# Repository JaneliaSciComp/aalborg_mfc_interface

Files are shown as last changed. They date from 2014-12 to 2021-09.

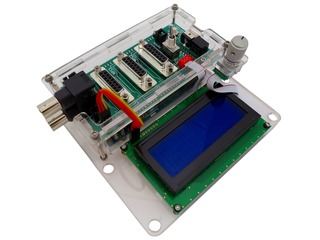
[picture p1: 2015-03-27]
images/aalborg_mfc_interface_03_s.jpg

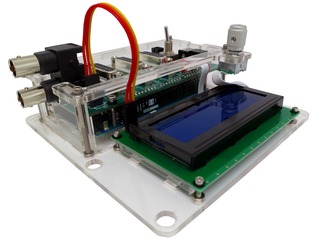
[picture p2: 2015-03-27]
images/aalborg_mfc_interface_04_s.jpg

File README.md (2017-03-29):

# aalborg_mfc_interface

Authors:

    Peter Polidoro <polidorop@janelia.hhmi.org>

License:

    BSD

## More Detailed Help on Installation and Usage

[modular-devices](https://github.com/janelia-modular-devices/modular-devices)

## Device Information

```json
{
  "method":"?",
  "device_info":{
    "name":"aalborg_mfc_interface",
    "model_number":1100,
    "serial_number":0,
    "firmware_version":{
      "major":0,
      "minor":1,
      "patch":0
    }
  },
  "methods":[
    "getMemoryFree",
    "resetDefaults",
    "setSerialNumber",
    "executeStandaloneCallback",
    "getLedsPowered",
    "setMfcFlow",
    "setMfcFlows",
    "getMfcFlowSetting",
    "getMfcFlowSettings",
    "getMfcFlowMeasure",
    "getMfcFlowMeasures",
    "getAnalogInput",
    "getAnalogInputs",
    "saveState",
    "recallState",
    "getSavedStates",
    "pulseBncB"
  ],
  "status":success
}
```

## Verbose Device Information

```json
{
  "method":"??",
  "device_info":{
    "name":"aalborg_mfc_interface",
    "model_number":1100,
    "serial_number":0,
    "firmware_version":{
      "major":0,
      "minor":1,
      "patch":0
    }
  },
  "methods":[
    {
      "name":"getMemoryFree",
      "parameters":[]
    },
    {
      "name":"resetDefaults",
      "parameters":[]
    },
    {
      "name":"setSerialNumber",
      "parameters":[
        {
          "name":"serial_number",
          "type":"long",
          "min":0,
          "max":65535
        }
      ]
    },
    {
      "name":"executeStandaloneCallback",
      "parameters":[]
    },
    {
      "name":"getLedsPowered",
      "parameters":[]
    },
    {
      "name":"setMfcFlow",
      "parameters":[
        {
          "name":"mfc",
          "type":"long",
          "min":0,
          "max":2
        },
        {
          "name":"percent",
          "type":"long",
          "min":0,
          "max":100
        }
      ]
    },
    {
      "name":"setMfcFlows",
      "parameters":[
        {
          "name":"percents",
          "type":"array",
          "array_element_type":"long",
          "min":0,
          "max":100
        }
      ]
    },
    {
      "name":"getMfcFlowSetting",
      "parameters":[
        {
          "name":"mfc",
          "type":"long",
          "min":0,
          "max":2
        }
      ]
    },
    {
      "name":"getMfcFlowSettings",
      "parameters":[]
    },
    {
      "name":"getMfcFlowMeasure",
      "parameters":[
        {
          "name":"mfc",
          "type":"long",
          "min":0,
          "max":2
        }
      ]
    },
    {
      "name":"getMfcFlowMeasures",
      "parameters":[]
    },
    {
      "name":"getAnalogInput",
      "parameters":[
        {
          "name":"ain",
          "type":"long",
          "min":0,
          "max":2
        }
      ]
    },
    {
      "name":"getAnalogInputs",
      "parameters":[]
    },
    {
      "name":"saveState",
      "parameters":[
        {
          "name":"state",
          "type":"long",
          "min":0,
          "max":9
        }
      ]
    },
    {
      "name":"recallState",
      "parameters":[
        {
          "name":"state",
          "type":"long",
          "min":0,
          "max":9
        }
      ]
    },
    {
      "name":"getSavedStates",
      "parameters":[]
    },
    {
      "name":"pulseBncB",
      "parameters":[
        {
          "name":"duration",
          "units":"ms",
          "type":"long",
          "min":1,
          "max":10000
        }
      ]
    }
  ],
  "status":success
}
```

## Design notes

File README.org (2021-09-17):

#+TITLE: aalborg_mfc_interface
#+AUTHOR: Peter Polidoro
#+EMAIL: peter@polidoro.io

* Repository Information
  - Author :: Peter Polidoro
  - License :: BSD

* More Detailed Help on Installation and Usage

   [[https://github.com/janelia-modular-devices/modular-devices][modular-devices]]

* Device Information

   #+BEGIN_SRC js
{
  "method":"?",
  "device_info":{
    "name":"aalborg_mfc_interface",
    "model_number":1100,
    "serial_number":0,
    "firmware_version":{
      "major":0,
      "minor":1,
      "patch":0
    }
  },
  "methods":[
    "getMemoryFree",
    "resetDefaults",
    "setSerialNumber",
    "executeStandaloneCallback",
    "getLedsPowered",
    "setMfcFlow",
    "setMfcFlows",
    "getMfcFlowSetting",
    "getMfcFlowSettings",
    "getMfcFlowMeasure",
    "getMfcFlowMeasures",
    "getAnalogInput",
    "getAnalogInputs",
    "saveState",
    "recallState",
    "getSavedStates",
    "pulseBncB"
  ],
  "status":success
}
   #+END_SRC

* Verbose Device Information

   #+BEGIN_SRC js
{
  "method":"??",
  "device_info":{
    "name":"aalborg_mfc_interface",
    "model_number":1100,
    "serial_number":0,
    "firmware_version":{
      "major":0,
      "minor":1,
      "patch":0
    }
  },
  "methods":[
    {
      "name":"getMemoryFree",
      "parameters":[]
    },
    {
      "name":"resetDefaults",
      "parameters":[]
    },
    {
      "name":"setSerialNumber",
      "parameters":[
        {
          "name":"serial_number",
          "type":"long",
          "min":0,
          "max":65535
        }
      ]
    },
    {
      "name":"executeStandaloneCallback",
      "parameters":[]
    },
    {
      "name":"getLedsPowered",
      "parameters":[]
    },
    {
      "name":"setMfcFlow",
      "parameters":[
        {
          "name":"mfc",
          "type":"long",
          "min":0,
          "max":2
        },
        {
          "name":"percent",
          "type":"long",
          "min":0,
          "max":100
        }
      ]
    },
    {
      "name":"setMfcFlows",
      "parameters":[
        {
          "name":"percents",
          "type":"array",
          "array_element_type":"long",
          "min":0,
          "max":100
        }
      ]
    },
    {
      "name":"getMfcFlowSetting",
      "parameters":[
        {
          "name":"mfc",
          "type":"long",
          "min":0,
          "max":2
        }
      ]
    },
    {
      "name":"getMfcFlowSettings",
      "parameters":[]
    },
    {
      "name":"getMfcFlowMeasure",
      "parameters":[
        {
          "name":"mfc",
          "type":"long",
          "min":0,
          "max":2
        }
      ]
    },
    {
      "name":"getMfcFlowMeasures",
      "parameters":[]
    },
    {
      "name":"getAnalogInput",
      "parameters":[
        {
          "name":"ain",
          "type":"long",
          "min":0,
          "max":2
        }
      ]
    },
    {
      "name":"getAnalogInputs",
      "parameters":[]
    },
    {
      "name":"saveState",
      "parameters":[
        {
          "name":"state",
          "type":"long",
          "min":0,
          "max":9
        }
      ]
    },
    {
      "name":"recallState",
      "parameters":[
        {
          "name":"state",
          "type":"long",
          "min":0,
          "max":9
        }
      ]
    },
    {
      "name":"getSavedStates",
      "parameters":[]
    },
    {
      "name":"pulseBncB",
      "parameters":[
        {
          "name":"duration",
          "units":"ms",
          "type":"long",
          "min":1,
          "max":10000
        }
      ]
    }
  ],
  "status":success
}
   #+END_SRC

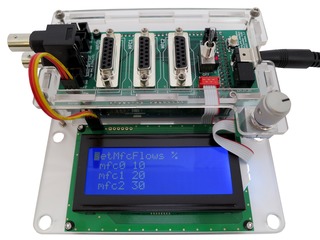
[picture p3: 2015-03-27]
images/aalborg_mfc_interface_06_s.jpg

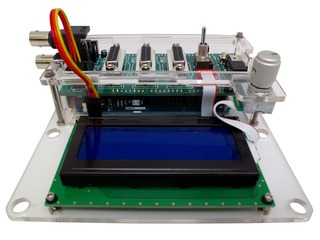
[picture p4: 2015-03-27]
images/aalborg_mfc_interface_05_s.jpg

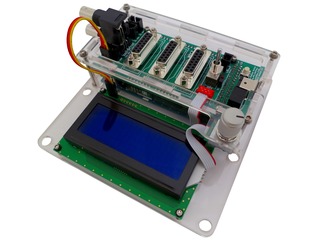
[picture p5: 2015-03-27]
images/aalborg_mfc_interface_01_s.jpg

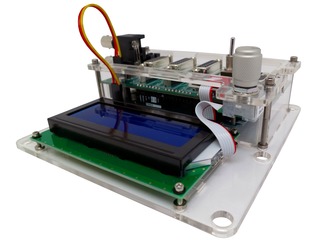
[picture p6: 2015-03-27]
images/aalborg_mfc_interface_02_s.jpg

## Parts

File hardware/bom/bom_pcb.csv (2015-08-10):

Item | Reference(s) | Value | Quantity | Description | PartNumber | Vendor
1 | ARDUINO1 | ARDUINO_MEGA | 1 | BOARD MCU MEGA2560 | 1050-1018-ND | digikey
2 | C1 C2 C3 C6 C7 C8 | 10uF | 6 | CAP CER 10UF 50V 10% X7S 1210 | 445-4536-1-ND | digikey
3 | C4 C5 | 0.1uF | 2 | CAP CER 0.1UF 50V 10% X7R 1210 | 478-3586-1-ND | digikey
4 | D1 | LED_24V | 1 | LED 2MM 24V VERTICAL RED PC MNT | 350-1723-ND | digikey
5 | E1 | ENCODER_C14 | 1 | CONN FMALE-ON-BRD 6POS VERT SMD | A99474CT-ND | digikey
6 | J1 J2 J3 | DB15FV | 3 | CONN D-SUB RCPT 15POS VERT GOLD | A102054-ND | digikey
7 | P1 | PWR_JACK_2.5x5.5 | 1 | CONN PWR JACK DC 2.5X5.5 8A T/H | CP-063BH-ND | digikey
8 | P2 | HEADER_01X03 | 1 | 01x03 .100 SR STRAIGHT | 609-3461-ND | digikey
9 | P3 | BNC_DOUBLE_RA | 1 | CONN BNC JACK R/A 75 OHM PCB | ACX1655-ND | digikey
10 | P4 P5 P6 | HEADER_01X03_SHR | 3 | CONN HEADER 3POS .100 VERT GOLD | WM4801-ND | digikey
11 | R1 R2 R3 R4 R5 | 5.11k | 5 | RES SMD 5.11K OHM 1% 1/2W 1210 | P5.11KAACT-ND | digikey
12 | REG1 | CONV_DC_DC_12V_1A | 1 | CONV DC/DC 1A 12V OUT SIP VERT | 945-1392-5-ND | digikey
13 | S1 | HEADER_01X02_SHR | 1 | CONN HEADER 2POS .100 VERT GOLD | WM4800-ND | digikey
14 | SW1 | DPST_SERIES_M | 1 | SWITCH TOGGLE DPST 6A 125V | 360-3244-ND | digikey
15 | SW2 | KT_SWITCH | 1 | SWITCH TACTILE SPST-NO 1VA 32V | CKN1860CT-ND | digikey
16 | U1 U2 | MAX6817 | 2 | IC DEBOUNCER SWITCH DUAL SOT23-6 | MAX6817EUT+TCT-ND | digikey

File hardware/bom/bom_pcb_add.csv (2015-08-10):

Item | Function | Quantity | Description | PartNumber | Vendor
1 | ARDUINO | 2 | CONN HDR VERT 50POS .100 SNGL | SAM1055-50-ND | digikey
2 | ARDUINO | 1 | CABLE USB A-B MALE 1M 2.0 VERS | AE1462-ND | digikey
3 | POWER | 1 | AC/DC DESKTOP ADAPTER 24V 100W | 271-2728-ND | digikey
4 | POWER | 1 | LINE CORD 3 COND US | 993-1039-ND | digikey
5 | DISPLAY | 1 | LCD SERIAL 4X20 SIDE WHT BKLT | NHD-0420D3Z-NSW-BBW-V3-ND | digikey
6 | DISPLAY | 1 | 01x03 .100 SR STRAIGHT | 609-3461-ND | digikey
7 | DISPLAY | 1 | Jumper Wire - 0.1in 3-pin 4in | PRT-10363 | sparkfun
8 | ENCODER_C14 | 1 | ENCODER OPT 32PPR DET CABLE TYPE | 102-1914-ND | digikey
9 | ENCODER_C14 | 1 | KNOB CLR/MATTE.50 DIA .250 SHAFT | 226-3100-ND | digikey
10 | MFC | 2 | ASSEMBLED D-SUB CABLE 15-POS | 277-7325-ND | digikey

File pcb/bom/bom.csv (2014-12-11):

Source: aalborg_mfc_interface.sch
Date: Wed 10 Dec 2014 05:16:41 PM EST
Item | Reference(s) | Value | Quantity | Description | PartNumber | Vendor
1 | ARDUINO1 | ARDUINO_MEGA | 1 | 1050-1018-ND | digikey
2 | C1 C2 C3 C5 C6 | 10uF | 5 | 445-4536-1-ND | digikey
3 | C4 | 0.1uF | 1 | 478-3586-1-ND | digikey
4 | D1 | LED_24V | 1 | 350-1723-ND | digikey
5 | E1 | ENCODER_C14 | 1 | 102-1914-ND | digikey
6 | J1 J2 | DB15FV | 2 | A102054-ND | digikey
7 | P1 | PWR_JACK_2.5x5.5 | 1 | CP-063BH-ND | digikey
8 | P2 | HEADER_01X03 | 1 | 609-3461-ND | digikey
9 | R1 R2 R3 R4 | 5.11k | 4 | P5.11KAACT-ND | digikey
10 | REG1 | CONV_DC_DC_12V_1A | 1 | 945-1392-5-ND | digikey
11 | U1 | MAX6817 | 1 | MAX6817EUT+TCT-ND | digikey

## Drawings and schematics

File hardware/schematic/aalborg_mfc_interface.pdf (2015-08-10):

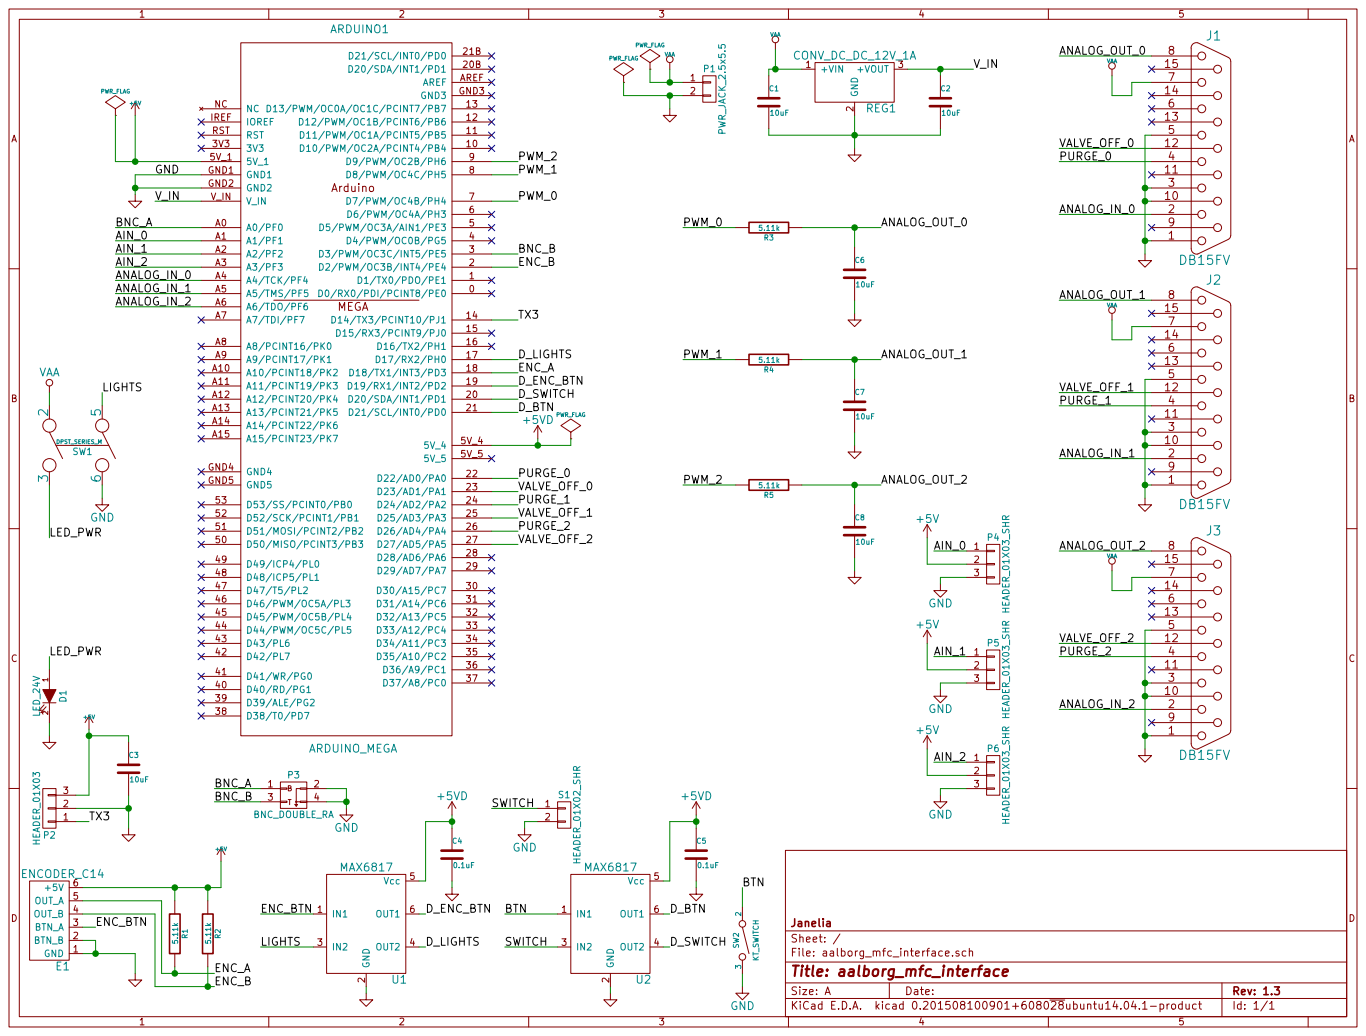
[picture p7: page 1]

File: aalborg_mfc_interface.sch Sheet: / Janelia

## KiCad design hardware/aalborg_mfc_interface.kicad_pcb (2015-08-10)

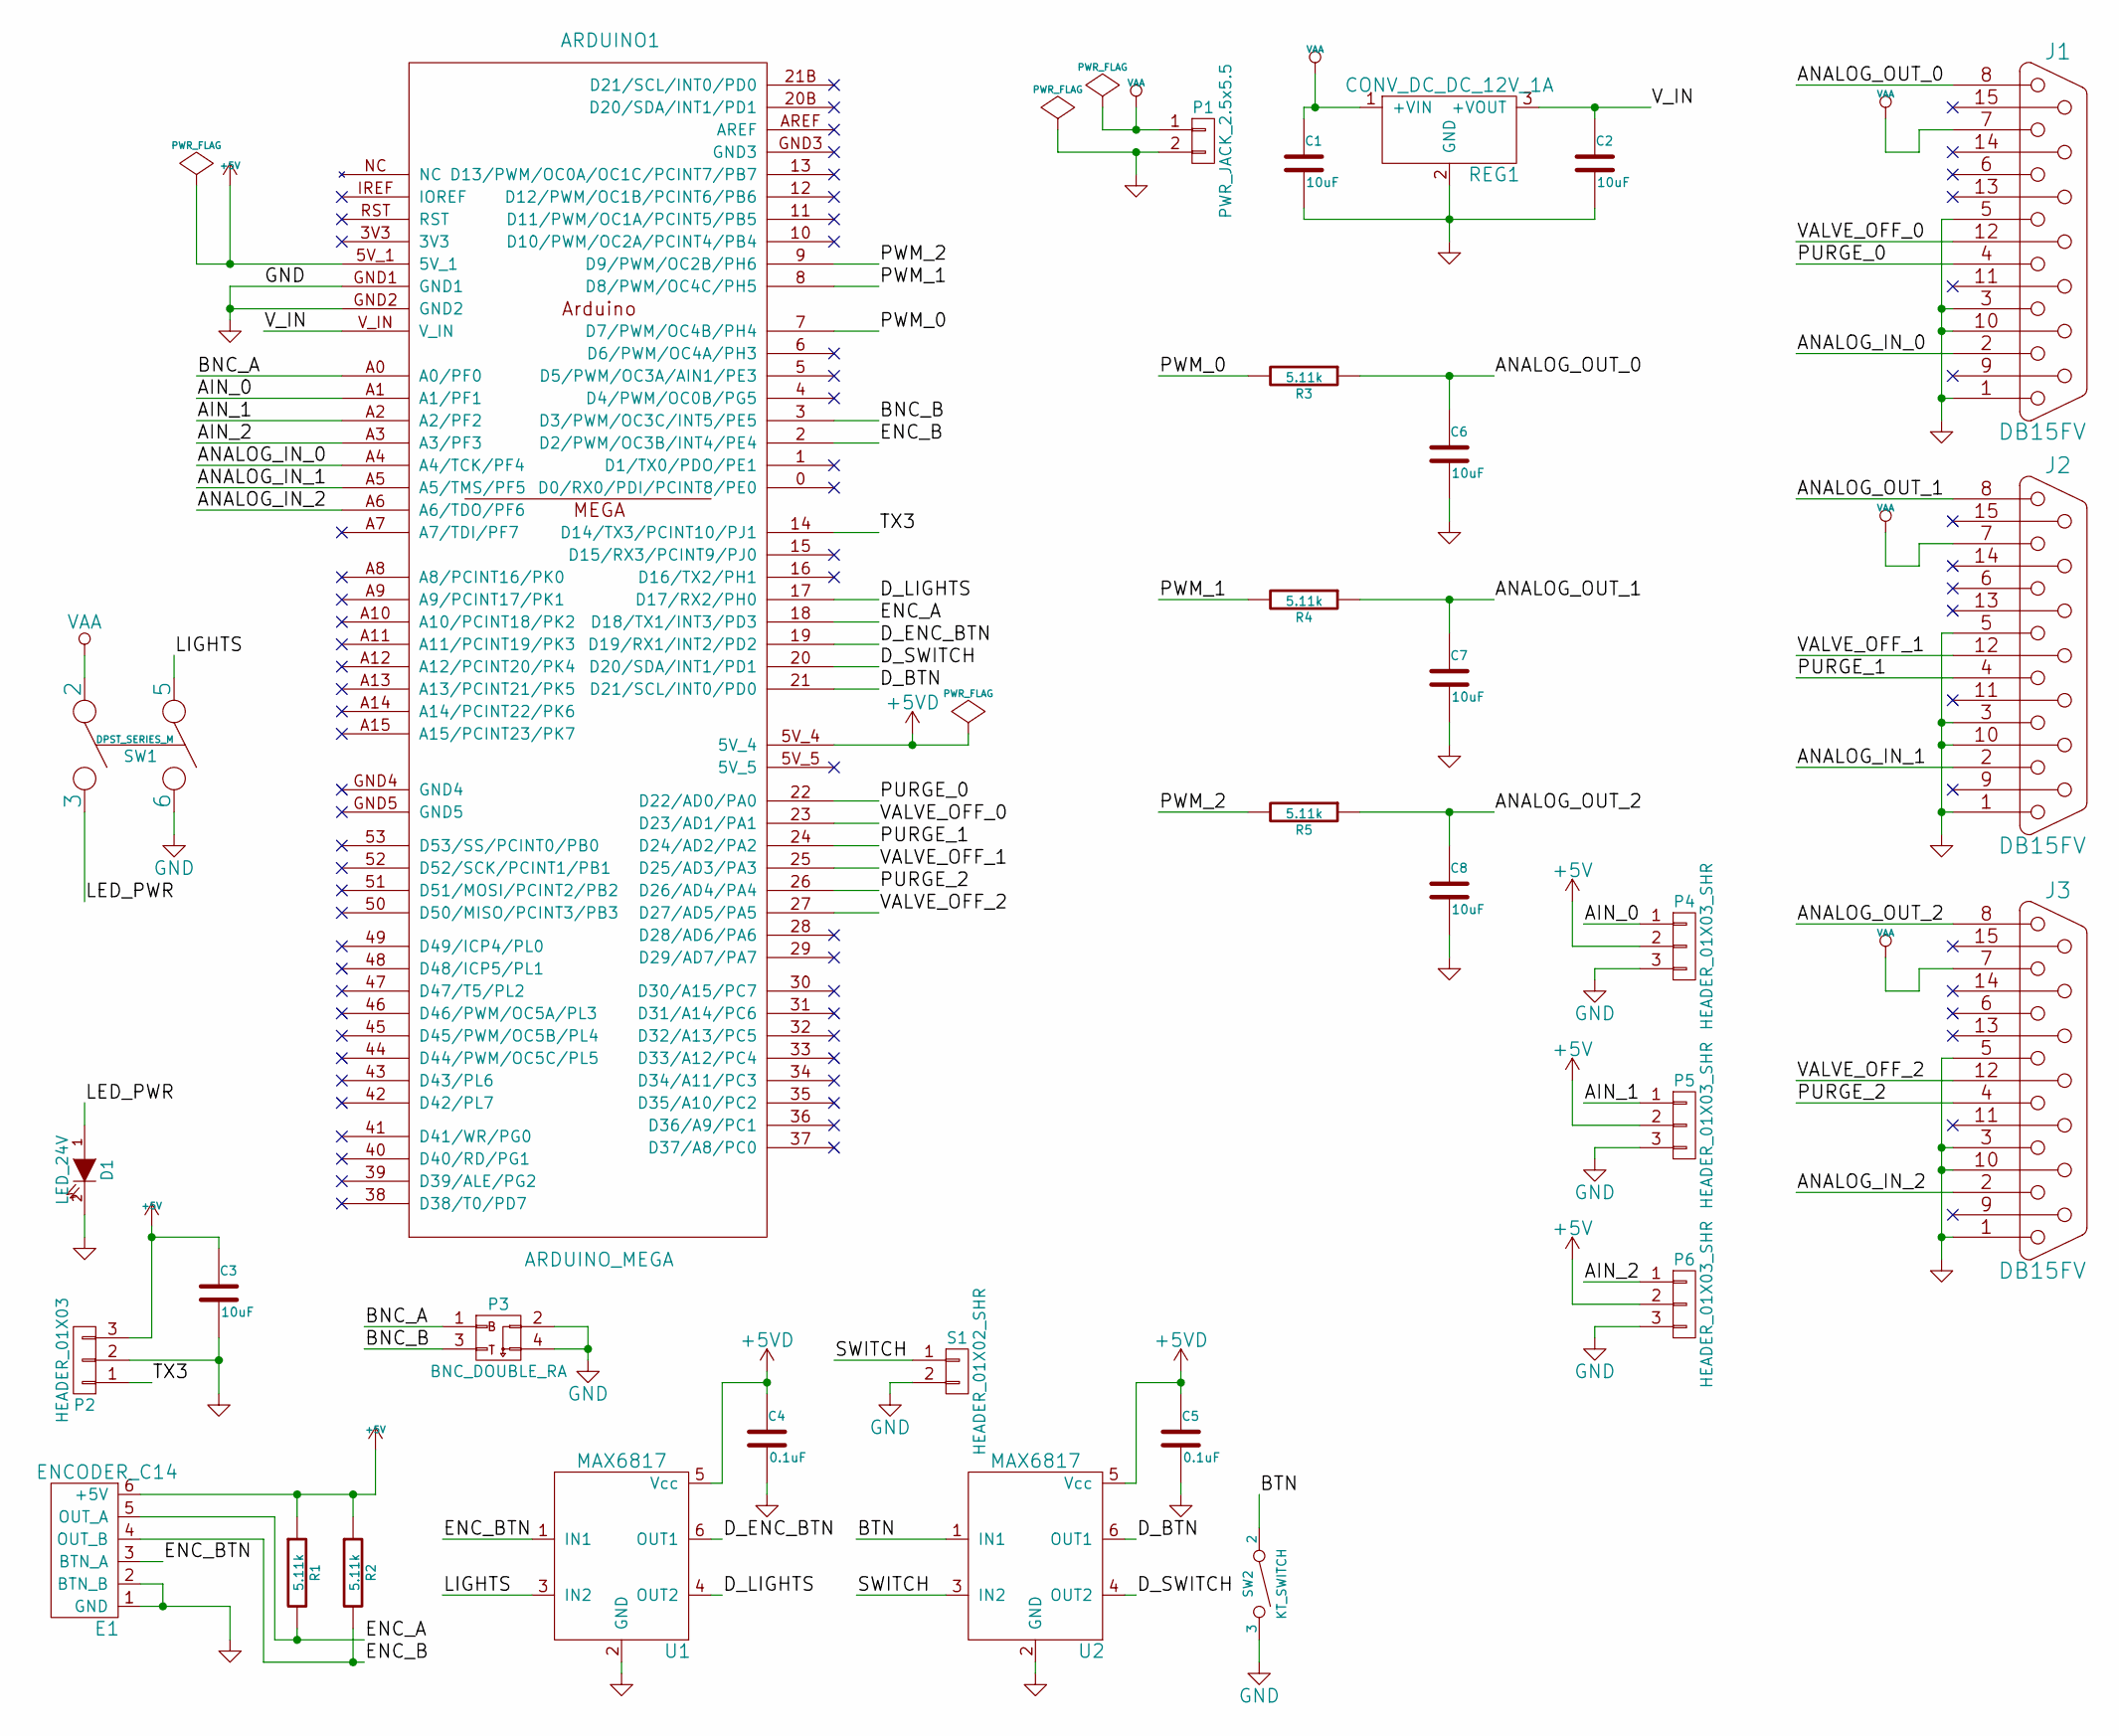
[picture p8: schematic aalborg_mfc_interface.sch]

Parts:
ARDUINO1: ARDUINO_MEGA; ARDUINO_MEGA_SHIELD; PartNumber 1050-1018-ND
C1, C2, C3, C6, C7, C8: 10uF; SM1210; PartNumber 445-4536-1-ND
C4, C5: 0.1uF; SM1210; PartNumber 478-3586-1-ND
D1: LED_24V; LED_555-3XXX; PartNumber 350-1723-ND
E1: ENCODER_C14; Micro-MaTch_6_SMD; PartNumber A99474CT-ND
J1, J2, J3: DB15FV; DB15FD; PartNumber A102054-ND
P1: PWR_JACK_2.5x5.5; DCJACK_2PIN_HIGHCURRENT; PartNumber CP-063BH-ND
P2: HEADER_01X03; Header_3_Pin; PartNumber 609-3461-ND
P3: BNC_DOUBLE_RA; BNC_DOUBLE; PartNumber ACX1655-ND
P4, P5, P6: HEADER_01X03_SHR; Header_Shrouded_3_Pin; PartNumber WM4801-ND
R1, R2, R3, R4, R5: 5.11k; SM1210; PartNumber P5.11KAACT-ND
REG1: CONV_DC_DC_12V_1A; DC_DC_CONV_R78C; PartNumber 945-1392-5-ND
S1: HEADER_01X02_SHR; Header_Shrouded_2_Pin; PartNumber WM4800-ND
SW1: DPST_SERIES_M; PartNumber 360-3244-ND
SW2: KT_SWITCH; PartNumber CKN1860CT-ND
U1, U2: MAX6817; PartNumber MAX6817EUT+TCT-ND

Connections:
+5V: ARDUINO1.5V_1, C3.1, E1.6 (+5V), P2.3, P4.2, P5.2, P6.2, R1.1, R2.1
+5VD: ARDUINO1.5V_4, C4.1, C5.1, U1.5 (Vcc), U2.5 (Vcc)
/AIN_0: ARDUINO1.A1 (A1/PF1), P4.1
/AIN_1: ARDUINO1.A2 (A2/PF2), P5.1
/AIN_2: ARDUINO1.A3 (A3/PF3), P6.1
/ANALOG_IN_0: ARDUINO1.A4 (A4/TCK/PF4), J1.2
/ANALOG_IN_1: ARDUINO1.A5 (A5/TMS/PF5), J2.2
/ANALOG_IN_2: ARDUINO1.A6 (A6/TDO/PF6), J3.2
/ANALOG_OUT_0: C6.1, J1.8, R3.1
/ANALOG_OUT_1: C7.1, J2.8, R4.1
/ANALOG_OUT_2: C8.1, J3.8, R5.1
/BNC_A: ARDUINO1.A0 (A0/PF0), P3.1
/BNC_B: ARDUINO1.3 (D3/PWM/OC3C/INT5/PE5), P3.3
/BTN: SW2.2, U2.1 (IN1)
/D_BTN: ARDUINO1.21 (D21/SCL/INT0/PD0), U2.6 (OUT1)
/D_ENC_BTN: ARDUINO1.19 (D19/RX1/INT2/PD2), U1.6 (OUT1)
/D_LIGHTS: ARDUINO1.17 (D17/RX2/PH0), U1.4 (OUT2)
/D_SWITCH: ARDUINO1.20 (D20/SDA/INT1/PD1), U2.4 (OUT2)
/ENC_A: ARDUINO1.18 (D18/TX1/INT3/PD3), E1.5 (OUT_A), R1.2
/ENC_B: ARDUINO1.2 (D2/PWM/OC3B/INT4/PE4), E1.4 (OUT_B), R2.2
/ENC_BTN: E1.3 (BTN_A), U1.1 (IN1)
/LED_PWR: D1.1 (A), SW1.3
/LIGHTS: SW1.5, U1.3 (IN2)
/PURGE_0: ARDUINO1.22 (D22/AD0/PA0), J1.4
/PURGE_1: ARDUINO1.24 (D24/AD2/PA2), J2.4
/PURGE_2: ARDUINO1.26 (D26/AD4/PA4), J3.4
/PWM_0: ARDUINO1.7 (D7/PWM/OC4B/PH4), R3.2
/PWM_1: ARDUINO1.8 (D8/PWM/OC4C/PH5), R4.2
/PWM_2: ARDUINO1.9 (D9/PWM/OC2B/PH6), R5.2
/SWITCH: S1.1, U2.3 (IN2)
/TX3: ARDUINO1.14 (D14/TX3/PCINT10/PJ1), P2.1
/VALVE_OFF_0: ARDUINO1.23 (D23/AD1/PA1), J1.12
/VALVE_OFF_1: ARDUINO1.25 (D25/AD3/PA3), J2.12
/VALVE_OFF_2: ARDUINO1.27 (D27/AD5/PA5), J3.12
/V_IN: ARDUINO1.V_IN, C2.1, REG1.3 (+VOUT)
GND: ARDUINO1.GND1, ARDUINO1.GND2, C1.2, C2.2, C3.2, C4.2, C5.2, C6.2, C7.2, C8.2, D1.2 (K), E1.1 (GND), E1.2 (BTN_B), J1.1, J1.3, J1.5, J1.10, J2.1, J2.3, J2.5, J2.10, J3.1, J3.3, J3.5, J3.10, P1.2, P2.2, P3.2, P3.4, P4.3, P5.3, P6.3, REG1.2 (GND), S1.2, SW1.6, SW2.3, U1.2 (GND), U2.2 (GND)
VAA: C1.1, J1.7, J2.7, J3.7, P1.1, REG1.1 (+VIN), SW1.2

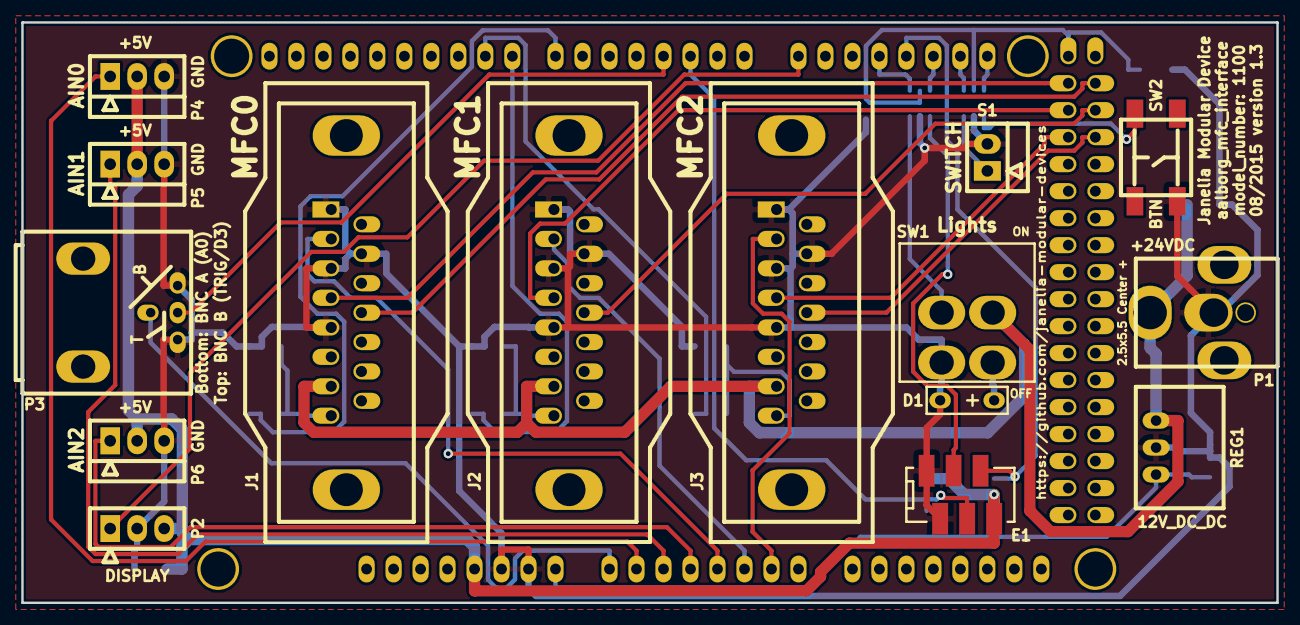
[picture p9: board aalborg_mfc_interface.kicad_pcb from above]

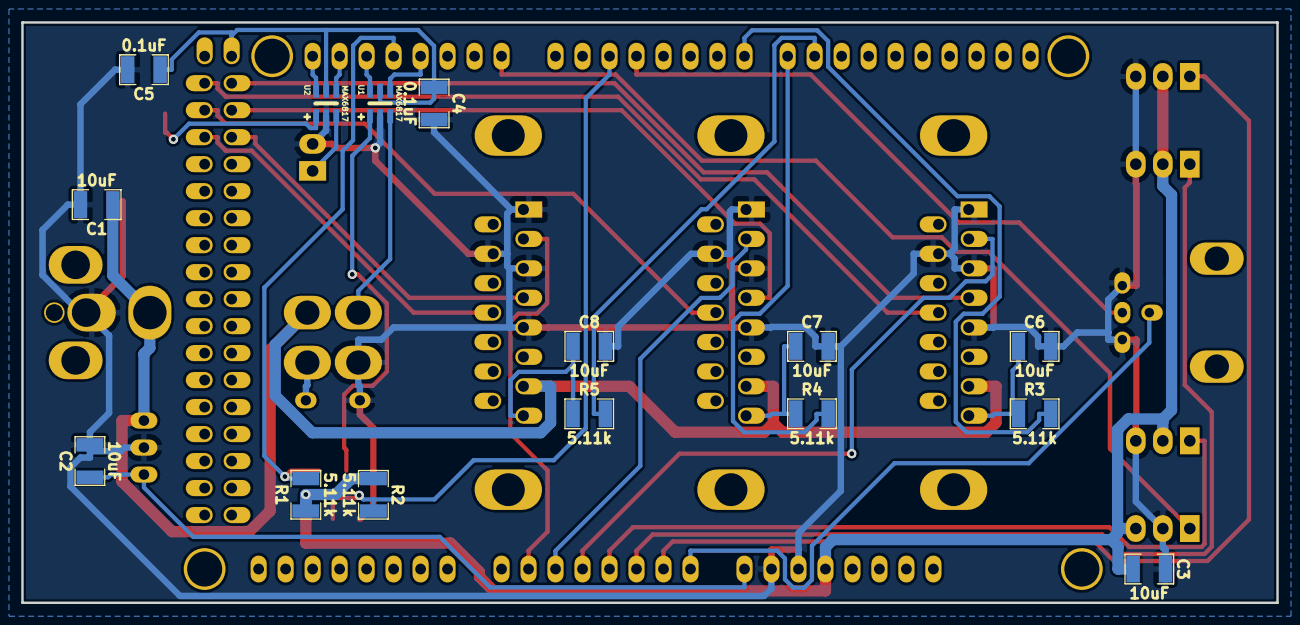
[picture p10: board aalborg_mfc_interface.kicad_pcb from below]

Board: 2 copper layers, 118.1 x 54.6 mm, 31 parts (15 on the bottom side), 37 nets.

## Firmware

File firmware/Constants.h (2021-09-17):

// ----------------------------------------------------------------------------
// Constants.h
//
//
// Authors:
// Peter Polidoro peter@polidoro.io
// ----------------------------------------------------------------------------
#ifndef CONSTANTS_H
#define CONSTANTS_H
#include "ConstantVariable.h"

namespace constants
{
enum {FRAME_COUNT=6};
enum {STATE_COUNT=10};
enum {MFC_COUNT=3};
enum {AIN_COUNT=3};

extern const unsigned int baudrate;

extern const unsigned int model_number;

extern const unsigned char firmware_major;
extern const unsigned char firmware_minor;
extern const unsigned char firmware_patch;

extern HardwareSerial & display_serial;

extern const int enc_a_pin;
extern const int enc_b_pin;
extern const int enc_btn_pin;
extern const int enc_btn_int;
extern const int btn_pin;
extern const int btn_int;
extern const int lights_pin;
extern const int bnc_b_pin;
extern const int standalone_update_period;

extern const int mfc_pwm_pins[MFC_COUNT];
extern const int mfc_ain_pins[MFC_COUNT];
extern const int mfc_purge_pins[MFC_COUNT];
extern const int mfc_valve_off_pins[MFC_COUNT];

extern const int ain_pins[AIN_COUNT];

extern const int pwm_min;
extern const int pwm_max;
extern const int ain_min;
extern const int ain_max;

extern const int percent_min;
extern const int percent_max;

extern const uint8_t states_array_default[STATE_COUNT][MFC_COUNT];

extern const uint8_t mfc_dsp_lbl_display_positions[MFC_COUNT];
extern const uint8_t ain_dsp_lbl_display_positions[AIN_COUNT];
extern const uint8_t state_dsp_lbl_display_position;
extern const uint8_t duration_dsp_lbl_display_position;

extern const uint8_t percent_display_width;

extern const uint8_t flow_var_display_positions[MFC_COUNT];
extern const uint8_t ain_dsp_var_display_positions[AIN_COUNT];
extern const uint8_t state_int_var_display_position;
extern const uint8_t duration_int_var_display_position;
extern const uint16_t duration_int_var_default;

extern const uint16_t duration_min;
extern const uint16_t duration_max;

extern ConstantString device_name;

extern ConstantString mfc_parameter_name;
extern ConstantString ain_parameter_name;
extern ConstantString percent_parameter_name;
extern ConstantString percents_parameter_name;
extern ConstantString state_parameter_name;
extern ConstantString duration_parameter_name;
extern ConstantString duration_parameter_units;

extern ConstantString execute_standalone_callback_method_name;
extern ConstantString get_leds_powered_method_name;
extern ConstantString set_mfc_flow_method_name;
extern ConstantString set_mfc_flows_method_name;
extern ConstantString get_mfc_flow_setting_method_name;
extern ConstantString get_mfc_flow_settings_method_name;
extern ConstantString get_mfc_flow_measure_method_name;
extern ConstantString get_mfc_flow_measures_method_name;
extern ConstantString get_analog_input_method_name;
extern ConstantString get_analog_inputs_method_name;
extern ConstantString save_state_method_name;
extern ConstantString recall_state_method_name;
extern ConstantString get_saved_states_method_name;
extern ConstantString pulse_bnc_b_method_name;

extern ConstantString states_name;
extern ConstantString frame0_name;
extern ConstantString frame1_name;
extern ConstantString frame2_name;
extern const ConstantString frame_name_array[FRAME_COUNT];
extern ConstantString mfc0_dsp_lbl_string;
extern ConstantString mfc1_dsp_lbl_string;
extern ConstantString mfc2_dsp_lbl_string;
extern const ConstantString mfc_dsp_lbl_strings[MFC_COUNT];
extern ConstantString ain0_dsp_lbl_string;
extern ConstantString ain1_dsp_lbl_string;
extern ConstantString ain2_dsp_lbl_string;
extern const ConstantString ain_dsp_lbl_strings[AIN_COUNT];
}
#endif

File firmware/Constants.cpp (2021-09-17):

// ----------------------------------------------------------------------------
// Constants.cpp
//
//
// Authors:
// Peter Polidoro peter@polidoro.io
// ----------------------------------------------------------------------------
#include "Constants.h"


namespace constants
{
const unsigned int baudrate = 9600;

const unsigned int model_number = 1100;

// Use semantic versioning http://semver.org/
const unsigned char firmware_major = 0;
const unsigned char firmware_minor = 1;
const unsigned char firmware_patch = 0;

HardwareSerial & display_serial = Serial3;

const int enc_a_pin = 18;
const int enc_b_pin = 2;
const int enc_btn_pin = 19;
const int enc_btn_int = 4;
const int btn_pin = 21;
const int btn_int = 2;
const int lights_pin = 17;
const int bnc_b_pin = 3;
const int standalone_update_period = 300;

const int mfc_pwm_pins[] = {7,8,9};
const int mfc_ain_pins[] = {4,5,6};
const int mfc_purge_pins[] = {22,24,26};
const int mfc_valve_off_pins[] = {23,25,27};

const int ain_pins[] = {1,2,3};

const int pwm_min = 0;
const int pwm_max = 255;
const int ain_min = 0;
const int ain_max = 1023;

const int percent_min = 0;
const int percent_max = 100;

const uint8_t states_array_default[STATE_COUNT][MFC_COUNT] = {0};

const uint8_t mfc_dsp_lbl_display_positions[] = {24,44,64};
const uint8_t ain_dsp_lbl_display_positions[] = {24,44,64};
const uint8_t state_dsp_lbl_display_position = 51;
const uint8_t duration_dsp_lbl_display_position = 49;

const uint8_t percent_display_width = 3;

const uint8_t flow_var_display_positions[] = {26,46,66};
const uint8_t ain_dsp_var_display_positions[] = {26,46,66};
const uint8_t state_int_var_display_position = 57;
const uint8_t duration_int_var_display_position = 51;
const uint16_t duration_int_var_default = 10;

const uint16_t duration_min = 1;
const uint16_t duration_max = 10000;

CONSTANT_STRING(device_name,"aalborg_mfc_interface");

CONSTANT_STRING(mfc_parameter_name,"mfc");
CONSTANT_STRING(ain_parameter_name,"ain");
CONSTANT_STRING(percent_parameter_name,"percent");
CONSTANT_STRING(percents_parameter_name,"percents");
CONSTANT_STRING(state_parameter_name,"state");
CONSTANT_STRING(duration_parameter_name,"duration");
CONSTANT_STRING(duration_parameter_units,"ms");

CONSTANT_STRING(execute_standalone_callback_method_name,"executeStandaloneCallback");
CONSTANT_STRING(get_leds_powered_method_name,"getLedsPowered");
CONSTANT_STRING(set_mfc_flow_method_name,"setMfcFlow");
CONSTANT_STRING(set_mfc_flows_method_name,"setMfcFlows");
CONSTANT_STRING(get_mfc_flow_setting_method_name,"getMfcFlowSetting");
CONSTANT_STRING(get_mfc_flow_settings_method_name,"getMfcFlowSettings");
CONSTANT_STRING(get_mfc_flow_measure_method_name,"getMfcFlowMeasure");
CONSTANT_STRING(get_mfc_flow_measures_method_name,"getMfcFlowMeasures");
CONSTANT_STRING(get_analog_input_method_name,"getAnalogInput");
CONSTANT_STRING(get_analog_inputs_method_name,"getAnalogInputs");
CONSTANT_STRING(save_state_method_name,"saveState");
CONSTANT_STRING(recall_state_method_name,"recallState");
CONSTANT_STRING(get_saved_states_method_name,"getSavedStates");
CONSTANT_STRING(pulse_bnc_b_method_name,"pulseBncB");

CONSTANT_STRING(states_name,"states");
CONSTANT_STRING(frame0_name,"setMfcFlows %");
CONSTANT_STRING(frame1_name,"getMfcFlowMeasures %");
CONSTANT_STRING(frame2_name,"getAnalogInputs %");
const ConstantString frame_name_array[] =
  {
    frame0_name,
    frame1_name,
    frame2_name,
    save_state_method_name,
    recall_state_method_name,
    pulse_bnc_b_method_name,
  };
CONSTANT_STRING(mfc0_dsp_lbl_string,"mfc0");
CONSTANT_STRING(mfc1_dsp_lbl_string,"mfc1");
CONSTANT_STRING(mfc2_dsp_lbl_string,"mfc2");
const ConstantString mfc_dsp_lbl_strings[] =
  {
    mfc0_dsp_lbl_string,
    mfc1_dsp_lbl_string,
    mfc2_dsp_lbl_string,
  };
CONSTANT_STRING(ain0_dsp_lbl_string,"ain0");
CONSTANT_STRING(ain1_dsp_lbl_string,"ain1");
CONSTANT_STRING(ain2_dsp_lbl_string,"ain2");
const ConstantString ain_dsp_lbl_strings[] =
  {
    ain0_dsp_lbl_string,
    ain1_dsp_lbl_string,
    ain2_dsp_lbl_string,
  };
}

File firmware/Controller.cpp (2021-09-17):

// ----------------------------------------------------------------------------
// Controller.cpp
//
// Authors:
// Peter Polidoro peter@polidoro.io
// ----------------------------------------------------------------------------
#include "Controller.h"

Controller::Controller() :
  standalone_interface_(Standalone::StandaloneInterface(constants::display_serial,
                                                        constants::enc_a_pin,
                                                        constants::enc_b_pin,
                                                        constants::enc_btn_pin,
                                                        constants::enc_btn_int,
                                                        constants::btn_pin,
                                                        constants::btn_int,
                                                        constants::lights_pin,
                                                        constants::standalone_update_period))
{
}

void Controller::setup()
{
  EventController::event_controller.setup();

  // Pin Setup
  for (int mfc = 0; mfc < constants::MFC_COUNT; mfc++)
  {
    pinMode(constants::mfc_purge_pins[mfc],INPUT);
    pinMode(constants::mfc_valve_off_pins[mfc],INPUT);
  }
  pinMode(constants::bnc_b_pin,OUTPUT);

  // Device Info
  modular_device.setName(constants::device_name);
  modular_device.setModelNumber(constants::model_number);
  modular_device.setFirmwareVersion(constants::firmware_major,constants::firmware_minor,constants::firmware_patch);

  // Saved Variables
  modular_device.createSavedVariable(constants::states_name,
                                     constants::states_array_default,
                                     constants::STATE_COUNT);

  int default_state = 0;
  modular_device.getSavedVariableValue(constants::states_name,flow_settings_array_,default_state);
  for (int mfc=0; mfc<constants::MFC_COUNT; mfc++)
  {
    setMfcFlow(mfc,flow_settings_array_[mfc]);
  }

  // Parameters
  ModularDevice::Parameter & mfc_parameter = modular_device.createParameter(constants::mfc_parameter_name);
  mfc_parameter.setRange(0,constants::MFC_COUNT-1);

  ModularDevice::Parameter & ain_parameter = modular_device.createParameter(constants::ain_parameter_name);
  ain_parameter.setRange(0,constants::AIN_COUNT-1);

  ModularDevice::Parameter & percent_parameter = modular_device.createParameter(constants::percent_parameter_name);
  percent_parameter.setRange(constants::percent_min,constants::percent_max);

  ModularDevice::Parameter & percents_parameter = modular_device.createParameter(constants::percents_parameter_name);
  percents_parameter.setTypeArray();
  percents_parameter.setRange(constants::percent_min,constants::percent_max);

  ModularDevice::Parameter & state_parameter = modular_device.createParameter(constants::state_parameter_name);
  state_parameter.setRange(0,constants::STATE_COUNT-1);

  ModularDevice::Parameter & duration_parameter = modular_device.createParameter(constants::duration_parameter_name);
  duration_parameter.setRange(constants::duration_min,constants::duration_max);
  duration_parameter.setUnits(constants::duration_parameter_units);

  // Methods
  ModularDevice::Method & execute_standalone_callback_method = modular_device.createMethod(constants::execute_standalone_callback_method_name);
  execute_standalone_callback_method.attachCallback(callbacks::executeStandaloneCallbackCallback);

  ModularDevice::Method & get_leds_powered_method = modular_device.createMethod(constants::get_leds_powered_method_name);
  get_leds_powered_method.attachCallback(callbacks::getLedsPoweredCallback);

  ModularDevice::Method & set_mfc_flow_method = modular_device.createMethod(constants::set_mfc_flow_method_name);
  set_mfc_flow_method.attachCallback(callbacks::setMfcFlowCallback);
  set_mfc_flow_method.addParameter(mfc_parameter);
  set_mfc_flow_method.addParameter(percent_parameter);

  ModularDevice::Method & set_mfc_flows_method = modular_device.createMethod(constants::set_mfc_flows_method_name);
  set_mfc_flows_method.attachCallback(callbacks::setMfcFlowsCallback);
  set_mfc_flows_method.addParameter(percents_parameter);

  ModularDevice::Method & get_mfc_flow_setting_method = modular_device.createMethod(constants::get_mfc_flow_setting_method_name);
  get_mfc_flow_setting_method.attachCallback(callbacks::getMfcFlowSettingCallback);
  get_mfc_flow_setting_method.addParameter(mfc_parameter);

  ModularDevice::Method & get_mfc_flow_settings_method = modular_device.createMethod(constants::get_mfc_flow_settings_method_name);
  get_mfc_flow_settings_method.attachCallback(callbacks::getMfcFlowSettingsCallback);

  ModularDevice::Method & get_mfc_flow_measure_method = modular_device.createMethod(constants::get_mfc_flow_measure_method_name);
  get_mfc_flow_measure_method.attachCallback(callbacks::getMfcFlowMeasureCallback);
  get_mfc_flow_measure_method.addParameter(mfc_parameter);

  ModularDevice::Method & get_mfc_flow_measures_method = modular_device.createMethod(constants::get_mfc_flow_measures_method_name);
  get_mfc_flow_measures_method.attachCallback(callbacks::getMfcFlowMeasuresCallback);

  ModularDevice::Method & get_analog_input_method = modular_device.createMethod(constants::get_analog_input_method_name);
  get_analog_input_method.attachCallback(callbacks::getAnalogInputCallback);
  get_analog_input_method.addParameter(ain_parameter);

  ModularDevice::Method & get_analog_inputs_method = modular_device.createMethod(constants::get_analog_inputs_method_name);
  get_analog_inputs_method.attachCallback(callbacks::getAnalogInputsCallback);

  ModularDevice::Method & save_state_method = modular_device.createMethod(constants::save_state_method_name);
  save_state_method.attachCallback(callbacks::saveStateCallback);
  save_state_method.addParameter(state_parameter);

  ModularDevice::Method & recall_state_method = modular_device.createMethod(constants::recall_state_method_name);
  recall_state_method.attachCallback(callbacks::recallStateCallback);
  recall_state_method.addParameter(state_parameter);

  ModularDevice::Method & get_saved_states_method = modular_device.createMethod(constants::get_saved_states_method_name);
  get_saved_states_method.attachCallback(callbacks::getSavedStatesCallback);

  ModularDevice::Method & pulse_bnc_b_method = modular_device.createMethod(constants::pulse_bnc_b_method_name);
  pulse_bnc_b_method.addParameter(duration_parameter);
  pulse_bnc_b_method.attachCallback(callbacks::pulseBncBCallback);

  // Start Server
  modular_device.startServer(constants::baudrate);

  // Standalone Interface
  standalone_interface_.setup(constants::frame_name_array,constants::FRAME_COUNT);

  // Display Labels
  Standalone::DisplayLabel * mfc_dsp_lbl_ptr_array[constants::MFC_COUNT];
  for (int mfc=0; mfc<constants::MFC_COUNT; mfc++)
  {
    mfc_dsp_lbl_ptr_array[mfc] = &(standalone_interface_.createDisplayLabel());
    mfc_dsp_lbl_ptr_array[mfc]->setDisplayPosition(constants::mfc_dsp_lbl_display_positions[mfc]);
    mfc_dsp_lbl_ptr_array[mfc]->setConstantString(constants::mfc_dsp_lbl_strings[mfc]);
    mfc_dsp_lbl_ptr_array[mfc]->setRightJustify();
  }
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

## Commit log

2014-11-25 Setup pcb schematic.
    [$aalborg_mfc_interface.sch, aalborg_mfc_interface.sch]
2014-11-25 Updated component library reference.
    [$aalborg_mfc_interface.sch]
2014-12-01 Added some schematic components.
    [aalborg_mfc_interface.sch]
2014-12-04 Initial board layout.
    [aalborg_mfc_interface.kicad_pcb, aalborg_mfc_interface.sch]
2014-12-05 Initial pcb layout.
    [aalborg_mfc_interface.dsn, aalborg_mfc_interface.kicad_pcb, aalborg_mfc_interface.sch]
2014-12-08 Finished pcb version 1.0.
    [aalborg_mfc_interface-B_Cu.gbl, aalborg_mfc_interface-B_Mask.gbs, aalborg_mfc_interface-B_SilkS.gbo, aalborg_mfc_interface-F_Cu.gtl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]
2014-12-10 Initial version 1.1 design.
    [aalborg_mfc_interface.kicad_pcb, aalborg_mfc_interface.sch]
2014-12-11 Added bom.csv.
    [bom.csv]
2014-12-11 Removed header and renamed bom.
    [bom_pcb.csv]
2014-12-11 Fixed missing Description field.
    [bom_pcb.csv]
2014-12-11 Updated line terminator to work on Windows as well.
    [bom_pcb.csv]
2014-12-11 Moved additional parts to new bom.
    [bom_pcb_add.csv]
2014-12-11 Removed extra symbols.
    [bom_pcb_add.csv]
2014-12-11 Cleaned up component descriptions.
    [aalborg_mfc_interface.kicad_pcb, aalborg_mfc_interface.sch, bom_pcb.csv]
2014-12-11 Updated descriptions.
    [bom_pcb_add.csv]
2014-12-11 Added order csv files.
    [digikey_order_pcb_add.csv, sparkfun_order_pcb_add.csv]
2014-12-11 Use automatically generated vendor order csv files.
    [digikey_order_pcb.csv]
2014-12-12 Updated ENCODER_C14.
    [aalborg_mfc_interface.kicad_pcb, aalborg_mfc_interface.sch, bom_pcb.csv, bom_pcb_add.csv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]
2015-01-05 Put model_number back on pcb silk screen.
    [aalborg_mfc_interface.kicad_pcb]
2015-01-08 Updated design with changes first made to power_switch_controller.
    [aalborg_mfc_interface.kicad_pcb, aalborg_mfc_interface.sch]
2015-01-13 Incremental changes towards version 1.1.
    [aalborg_mfc_interface.kicad_pcb, aalborg_mfc_interface.sch]
2015-01-14 Progress on pcb 1.1 design and firmware 1.0.
    [aalborg_mfc_interface.kicad_pcb, aalborg_mfc_interface.sch]
2015-01-16 Progress towards pcb v1.1.
    [aalborg_mfc_interface-B_Cu.gbl, aalborg_mfc_interface-B_Mask.gbs, aalborg_mfc_interface-B_SilkS.gbo, aalborg_mfc_interface-F_Cu.gtl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]
2015-01-20 Finished pcb v1.1.
    [aalborg_mfc_interface-B_Cu.gbl, aalborg_mfc_interface-B_Mask.gbs, aalborg_mfc_interface-B_SilkS.gbo, aalborg_mfc_interface-F_Cu.gtl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]
2015-01-20 Minor changes to names.
    [aalborg_mfc_interface.kicad_pcb, aalborg_mfc_interface.sch, bom_pcb.csv]
2015-01-28 remote -> modular.
    [aalborg_mfc_interface.kicad_pcb]
2015-02-19 Assembled DisplayElements into arrays.
2015-02-19 Added StandaloneInterface frames and callback functions.
2015-02-23 Added StandAlone frames.
    [aalborg_mfc_interface.sch]
2015-02-23 Finished pcb v1.2.
    [aalborg_mfc_interface-B_Cu.gbl, aalborg_mfc_interface-B_Mask.gbs, aalborg_mfc_interface-B_SilkS.gbo, aalborg_mfc_interface-F_Cu.gtl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]
2015-03-19 StandardCplusplus -> Array. Updated pin constants.
2015-07-13 JaneliaSciComp -> janelia-modular-devices.
    [aalborg_mfc_interface.kicad_pcb]
2015-08-10 Tiny changes to create v1.3.
    [aalborg_mfc_interface-B_Cu.gbl, aalborg_mfc_interface-B_Mask.gbs, aalborg_mfc_interface-B_SilkS.gbo, aalborg_mfc_interface-F_Cu.gtl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]
2015-08-10 SPST switch -> DPST switch.
    [aalborg_mfc_interface-B_Cu.gbl, aalborg_mfc_interface-B_Mask.gbs, aalborg_mfc_interface-B_SilkS.gbo, aalborg_mfc_interface-F_Cu.gtl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]
2015-08-10 Updated digikey_order_pcb_add.
    [digikey_order_pcb_add.csv]
2015-09-09 led_pwr_pin -> lights_pin.
2016-09-21 pcb -> hardware.
    [aalborg_mfc_interface-B_Cu.gbl, aalborg_mfc_interface-B_Mask.gbs, aalborg_mfc_interface-B_SilkS.gbo, aalborg_mfc_interface-F_Cu.gtl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]
